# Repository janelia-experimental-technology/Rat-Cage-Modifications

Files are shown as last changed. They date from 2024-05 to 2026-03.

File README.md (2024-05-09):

# Rat-Cage-Modifications
Documents the process of modifying Tecniplast cage lids to better suit rats with electrophysiology implants.

Designed at HHMI's Janelia research campus by the jET team, the modifications allow more space inside the home cage for rats with head mounted electrophysiology implants. The cages as purchased position the water bottle spouts too low in areas of the cage where there is not enough space for the rats to comfortably drink.  

Advantages: More space for the rat to comfortably move around the cage. 

Construction: The cage modifications include cutting out the original bottle holder sections of the lid, and installing several machined, and sheetmetal parts that are riveted to the cage and sealed with epoxy. 

See the individual part drawings for more detail on fabricating each part. See the attached assembly files and instructions with parts list including purchased commercial items needed to complete the tcage modifications. There are two designs documented in this repo: the V1 rat cage lid modifications from 2018, and the V2 modifications implemented in 2021. The V1 changes are simpler and require fewer custom parts. However, the V1 water bottle holders do not last as long under autoclave sterilization as the V2 version. 

Operation: The cage can be used normally after modification, cleaned,  and sterilized via autoclave.

Opportunity: Free to make for Non-Profit Research by downloading the design here. See included hardware license.

Rights and designs available for Commercial License. Janelia makes no endorsements or guarantees of licensee products.

For inquiries, please contact innovation@janelia.hhmi.org and reference this repository.

To cite the designs, please use DOI: https://doi.org/10.25378/janelia.25750719

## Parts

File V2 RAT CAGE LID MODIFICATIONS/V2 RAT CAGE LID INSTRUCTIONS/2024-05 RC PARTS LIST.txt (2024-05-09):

Rat Cage Parts List
Main Folder: $/DATA/PROJECTS/_PROJECTS BY LAB/VIVARIUM/RAT CAGE MODIFICATIONS/
Quotes folder: */FINAL ORDER/QUOTES

1)	97524A030, Sealing Rivets, Aluminum, 0.063"-0.125", 100ct
	Qty: 18 for bottle-side, 10 for non-bottle-side, 28 total per cage 
	Desc: Binds metal brackets and bottle holder weldment to Ultem panels
	https://www.mcmaster.com/97524A030/

2)	97524A031, Sealing Rivets, Aluminum, 0.126"-0.187", 100ct
	Qty: 12 for each side, 24 total per cage
	Desc: Binds Ultem panels to cage lid. Back with 94589A617 washers to protect cage from cracking
	https://www.mcmaster.com/97524A031/

3)	94589A617, Washers, Aluminum, #4, 100ct
	Qty: 12 for each side, 24 total per cage
	Desc: Backed against 97524A031 rivets to protect plastic from cracking
	https://www.mcmaster.com/94589A617/

4)	7467A65, Adhesive, 3M DP125, 1.64oz, Gray
	Desc: Use to fill gap between panels and lid
	https://www.mcmaster.com/7467A65/

5)	7467A73, Taper Tip Mixer Nozzle for 1.64oz
	Desc: Use with DP125
	https://www.mcmaster.com/7467A73/

6)	7467A15, Air-powered Dispensing Gun
	https://www.mcmaster.com/7467A15/

7)	J009837, RC PANEL FRONT FOR BOTTLE
	Qty: 1 per cage
	Desc: Holds bottle holder weldment to cage lid
	Material: https://www.mcmaster.com/8685K44/
	Machining: made in house at HHMI, you will need to quote with machine shop

8)	J009838, RC PANEL SIDE
	Qty: 2 per cage
	Desc: Side pieces, 1 on each side of the cage lid
	Material: https://www.mcmaster.com/8685K44/
	Machining: made in house at HHMI, you will need to quote with machine shop

9)	J009859, RC PANEL FRONT
	Qty: 1 per cage
	Desc: Front panel, used on the end of the cage lid that doesn't hold a bottle
	Material: https://www.mcmaster.com/8685K44/
	Machining: made in house at HHMI, you will need to quote with machine shop

10)	J008644 revA, RCBH4 WELDMENT
	Qty: 1 per cage
	Desc: Bottle holder weldment. Mounts to J009837
	Reorder: GoProto 84701 for hardware, Able 7269-0-AAA for electropolishing
	Modifications: See Drawings

11)	J009835 RC BRACKET LONG
	Qty: 2 per cage
	Desc: Mounts RC PANEL SIDE to RC PANEL FRONT (FOR BOTTLE)
	Reorder: GoProto 85475

12)	J009836 RC BRACKET SIDE
	Qty: 2 per cage
	Desc: Mounts RC PANEL SIDE to rat cage lid
	Reorder: GoProto 85475

13)	J009600 RC BRACKET FRONT
	Qty: 2 per cage
	Desc: Mounts RC PANEL FRONT (FOR BOTTLE) to rat cage lid
	Reorder: GoProto 85475

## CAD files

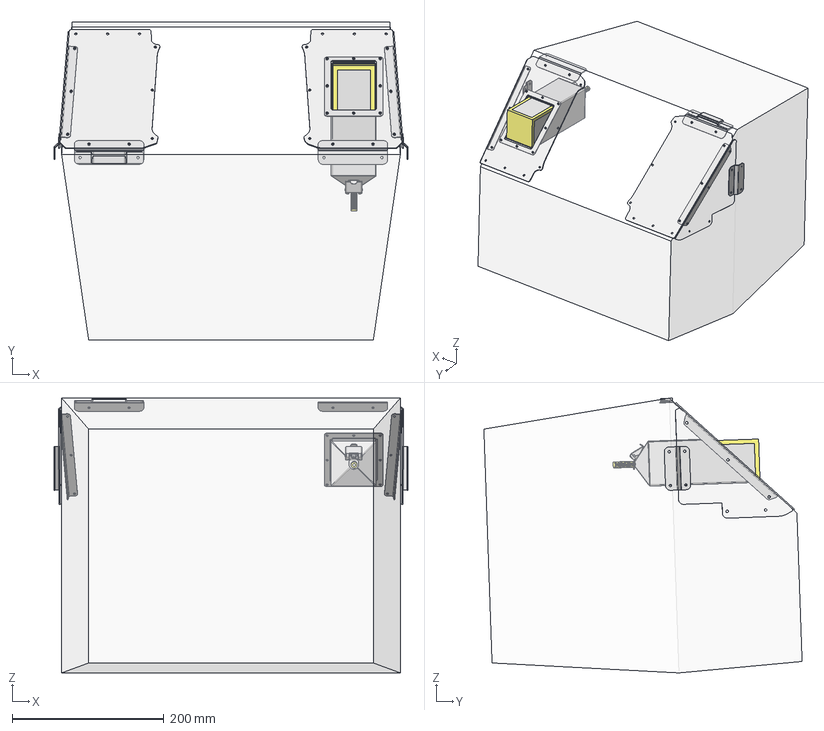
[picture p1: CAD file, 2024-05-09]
V2 RAT CAGE LID MODIFICATIONS/V2 RAT CAGE LID ASSEMBLY MODELS/RC ASSY.stp
465.9 x 418.9 x 361.7 mm
J009600 x 2
J009837
J009859
J009838 x 2
J008644_1
J008639 x 2
J008640
J008642
J008641
J008643
RAT CAGE
J009835 x 2
J009836 x 2
RAT CAGE BOTTLE
RAT CAGE FLAP COVER
RAT CAGE FLAP ROD
RAT CAGE FLAP SPRING
RAT CAGE FLAP
J010308

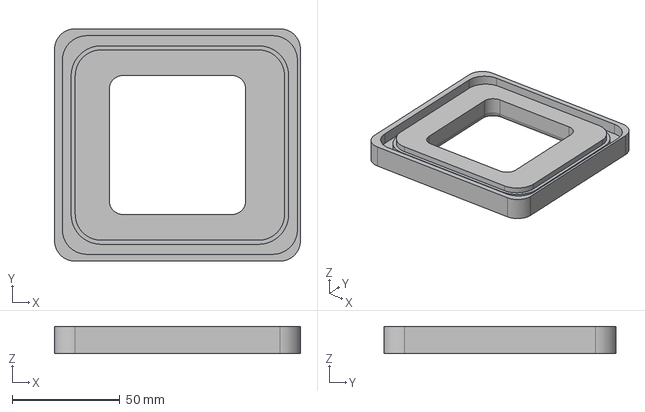
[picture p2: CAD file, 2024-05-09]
V1 RAT CAGE LID MODIFICATIONS/V1 RAT CAGE PART MODELS AND DRAWINGS/RAT WATER BOTTLE TRANSITION.stp
114.3 x 107.9 x 12.7 mm

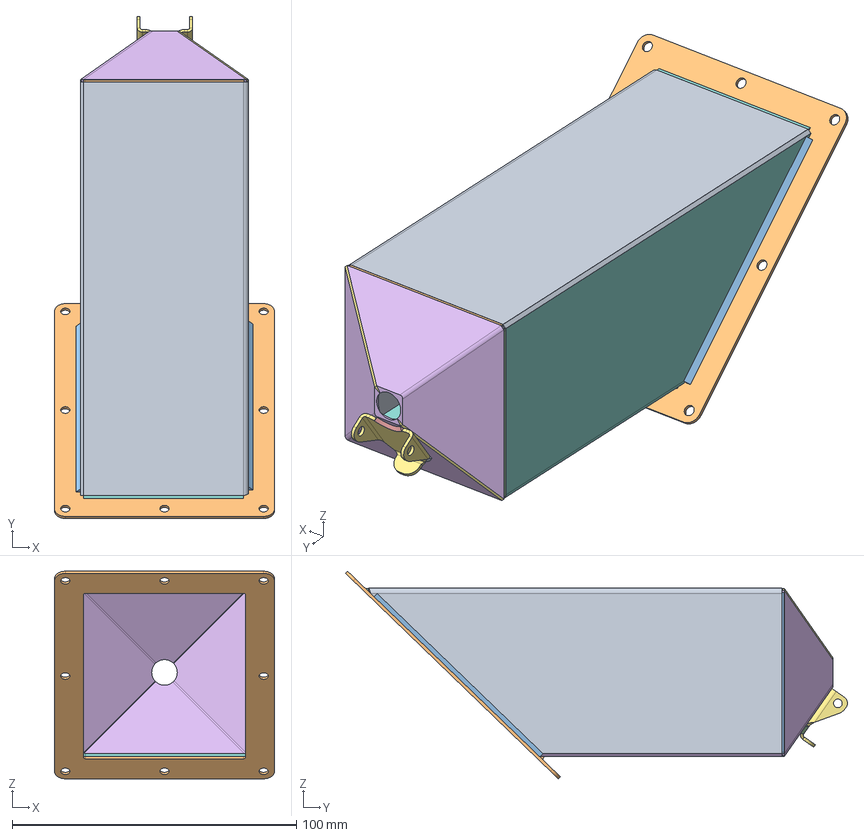
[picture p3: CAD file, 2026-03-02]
V2 RAT CAGE LID MODIFICATIONS/V2 RAT CAGE LID PART MODELS AND DRAWINGS/RCBH4 WELDMENT revC.stp
77.5 x 176.8 x 73.1 mm
J008644_1
J008639
J008640
J008642
J008641
J008639_1
J008643

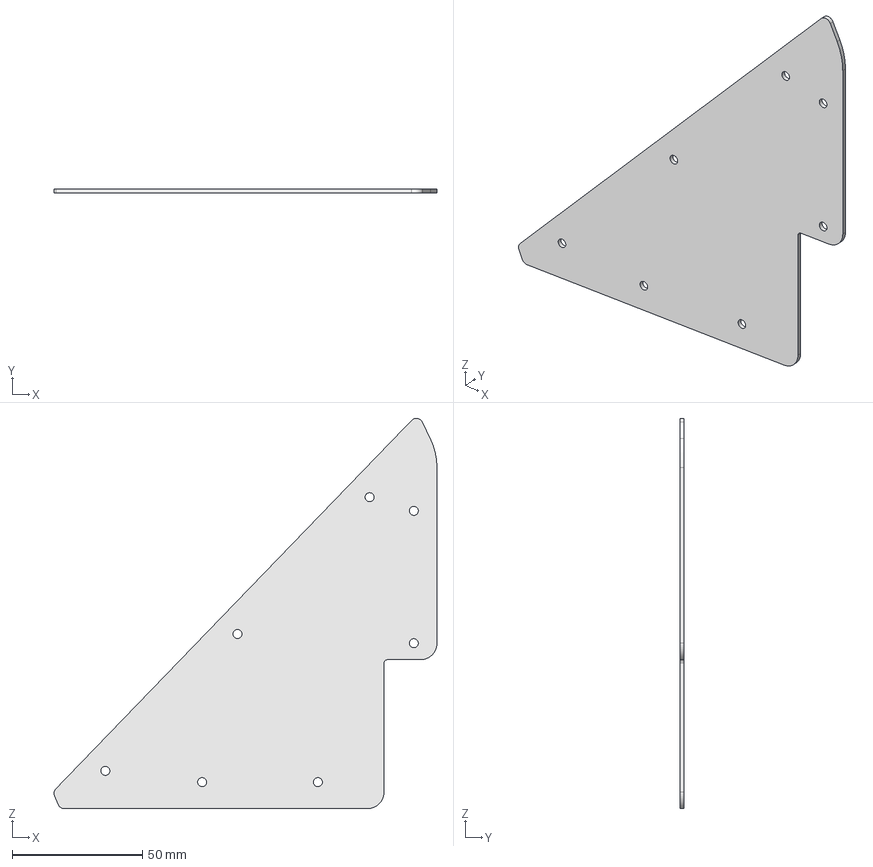
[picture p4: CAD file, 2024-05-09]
V1 RAT CAGE LID MODIFICATIONS/V1 RAT CAGE PART MODELS AND DRAWINGS/RC PANEL SIDE J009838.stp
147.0 x 1.59 x 149.8 mm

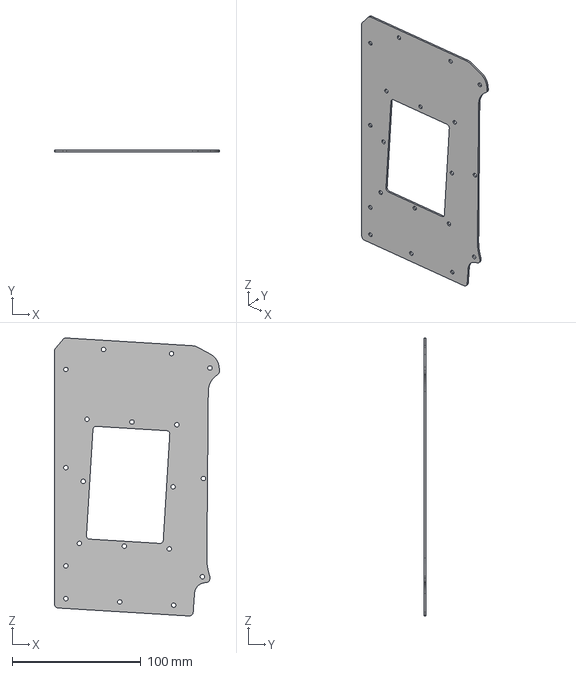
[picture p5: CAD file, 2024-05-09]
V2 RAT CAGE LID MODIFICATIONS/V2 RAT CAGE LID PART MODELS AND DRAWINGS/RC PANEL FRONT FOR BOTTLE J009837.stp
128.1 x 1.59 x 215.7 mm

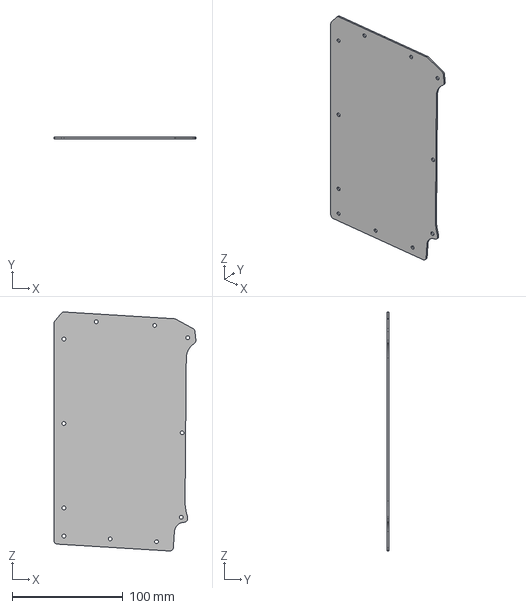
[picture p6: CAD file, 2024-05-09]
V1 RAT CAGE LID MODIFICATIONS/V1 RAT CAGE PART MODELS AND DRAWINGS/RC PANEL FRONT J009859.stp
128.1 x 1.59 x 215.7 mm

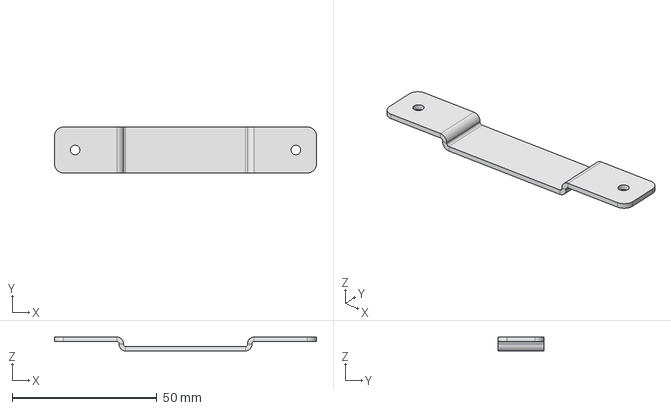
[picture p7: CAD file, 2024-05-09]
V1 RAT CAGE LID MODIFICATIONS/V1 RAT CAGE PART MODELS AND DRAWINGS/CARD HOLDER BRACKET J010308.stp
90.4 x 15.9 x 4.83 mm

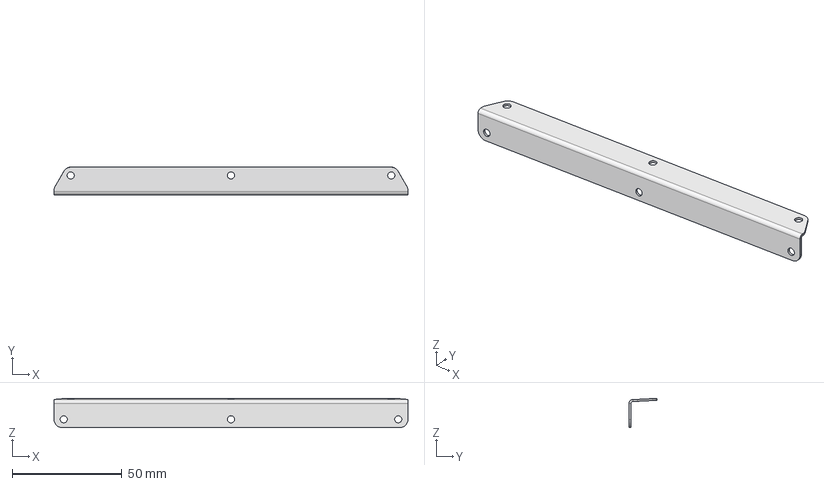
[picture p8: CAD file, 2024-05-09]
V1 RAT CAGE LID MODIFICATIONS/V1 RAT CAGE PART MODELS AND DRAWINGS/RC BRACKET LONG.stp
161.3 x 12.7 x 13.4 mm

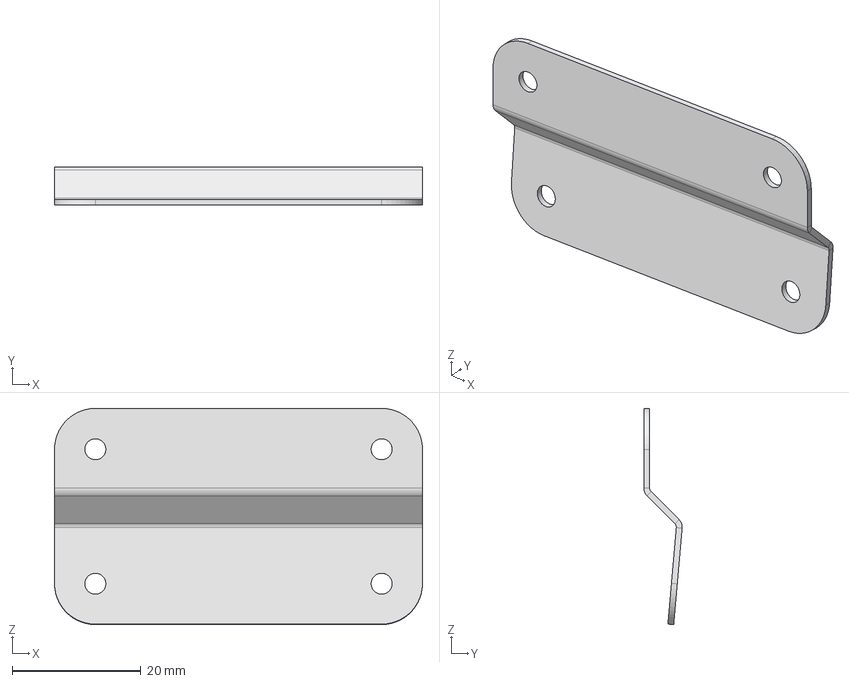
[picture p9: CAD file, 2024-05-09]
V1 RAT CAGE LID MODIFICATIONS/V1 RAT CAGE PART MODELS AND DRAWINGS/RC BRACKET SIDE.stp
57.1 x 5.97 x 33.6 mm

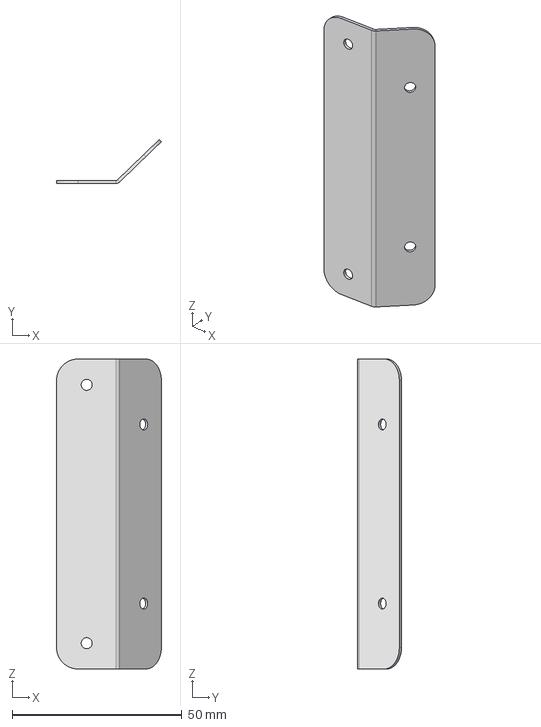
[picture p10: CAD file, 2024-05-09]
V1 RAT CAGE LID MODIFICATIONS/V1 RAT CAGE PART MODELS AND DRAWINGS/RC BRACKET FRONT.stp
30.9 x 13.0 x 91.4 mm

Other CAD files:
V2 RAT CAGE LID MODIFICATIONS/V2 RAT CAGE LID PART MODELS AND DRAWINGS/RCBH4 WELDMENT.dwg
V2 RAT CAGE LID MODIFICATIONS/V2 RAT CAGE LID PART MODELS AND DRAWINGS/RC PANEL FRONT FOR BOTTLE.dwg
V1 RAT CAGE LID MODIFICATIONS/V1 RAT CAGE PART MODELS AND DRAWINGS/RC PANEL FRONT.dwg
V1 RAT CAGE LID MODIFICATIONS/V1 RAT CAGE PART MODELS AND DRAWINGS/RC PANEL SIDE.dwg
V1 RAT CAGE LID MODIFICATIONS/V1 RAT CAGE PART MODELS AND DRAWINGS/CARD HOLDER BRACKET.dwg
V1 RAT CAGE LID MODIFICATIONS/V1 RAT CAGE PART MODELS AND DRAWINGS/CARD HOLDER BRACKET.ipt
V1 RAT CAGE LID MODIFICATIONS/V1 RAT CAGE PART MODELS AND DRAWINGS/RAT WATER BOTTLE TRANSITION.dwg
V1 RAT CAGE LID MODIFICATIONS/V1 RAT CAGE PART MODELS AND DRAWINGS/RAT WATER BOTTLE TRANSITION.ipt
V1 RAT CAGE LID MODIFICATIONS/V1 RAT CAGE PART MODELS AND DRAWINGS/RC BRACKET FRONT.dwg
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

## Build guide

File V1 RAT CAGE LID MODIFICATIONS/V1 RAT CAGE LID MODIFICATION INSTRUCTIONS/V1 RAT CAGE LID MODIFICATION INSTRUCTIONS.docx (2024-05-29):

Rat Cage Lid Modification Procedure

Parts List:

Name | Part Number | Vendor / Part Type | Qty / Unit
Rat Cage Lid | | Purchased-Techniplast | 1
RC Panel Front | J009859 | Custom machined | 1
RC Panel Side | J009838 | Custom machined | 1
RC Bracket Front | J009600 | Custom sheetmetal-GoProto | 1
RC Bracket Long | J009835 | Custom sheetmetal-GoProto | 1
RC Bracket Side | J009836 | Custom sheetmetal-GoProto | 1
Card Holder Bracket | J010308 | Custom sheetmetal-GoProto | 1
bottom taper section of right water bottle holder | | Purchased-Part of Techniplast Lid | 1
Rat Water Bottle Transition | | Custom machined | 1
Rivets - .063” - .125” | 97447A015 | McMaster | 10
Rivets - .126” - .187” | 97447A020 | McMaster | 10
Rivets - .188” - .25” | 97447A025 | McMaster | 2
18-8 SS No. 4 Washer | 98019A309 | McMaster | 8
18-8 SS No. 5 Washer | 90945A712 | McMaster | 10
Epoxy, 3M DP125 | 7467A65 | McMaster | 1

Tools List:

Name | Part Number | Vendor | Quantity/Unit
Angle Grinder/Dremel
1/8” Drill Bit
#28 Drill Bit

Power Drill
Pliers
Epoxy Applicator Gun | 74695A71 | McMaster | 1
Masking Tape | | | 1
Binder Clips (optional) | | | 2

Procedure

1. Cut Cage Lid
  a. Cut water bottle holder sections off the lid – cut lines shown in red on right picture
  b. The left and right sides will be cut at different locations

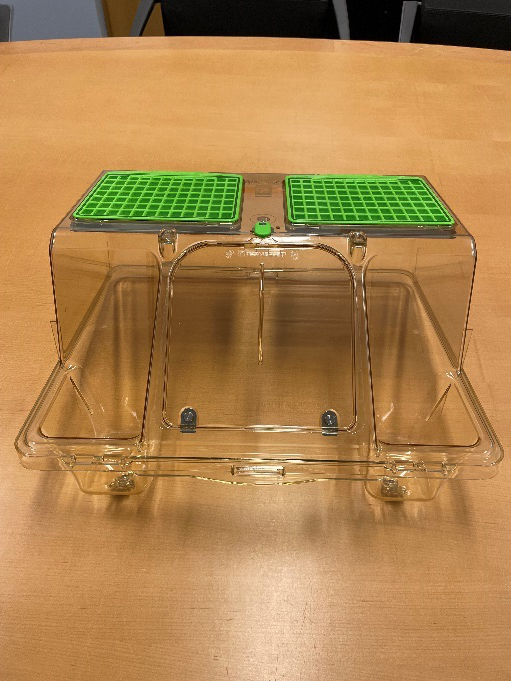
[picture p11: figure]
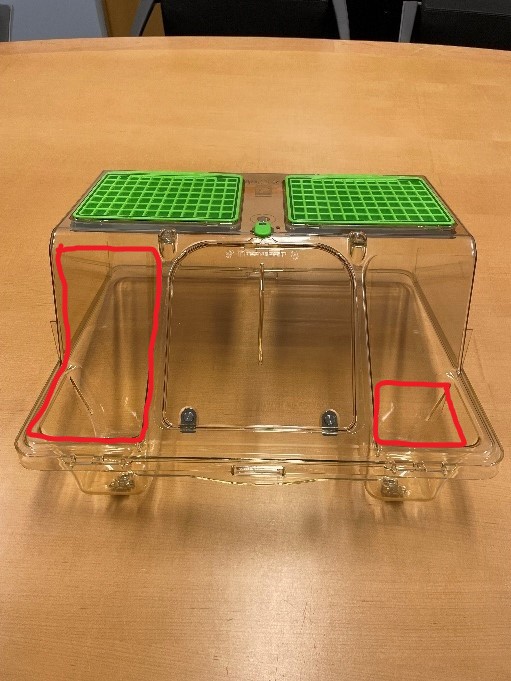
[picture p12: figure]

  c. Cut right bottle holder section at thick red line in photo below – there will be a natural seam to follow
  d. Save the bottom taper section of the holder and metal flap assembly and for reattachment to modified cage

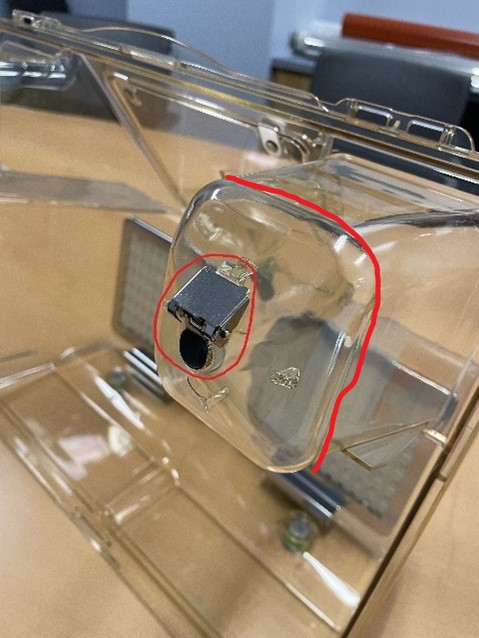
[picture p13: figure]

  e. Grind off the front card holder on the left side of the cage

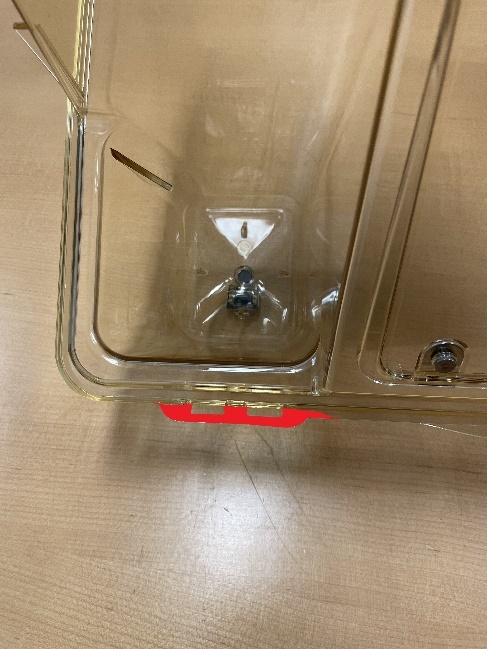
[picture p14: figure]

2. Assemble Flat Cover

Parts:

Part Number | Quantity
J009859 | 1
J009838 | 1
J009600 | 1
J009835 | 1
J009836 | 1
97447A015 | 10
90945A712 | 2

  a. Rivet front panel (J009859) and side panel (J009838) together using the long bracket (J009835) and six 97447A015 rivets
    i. Proper orientation of the panels, with respect to each other:

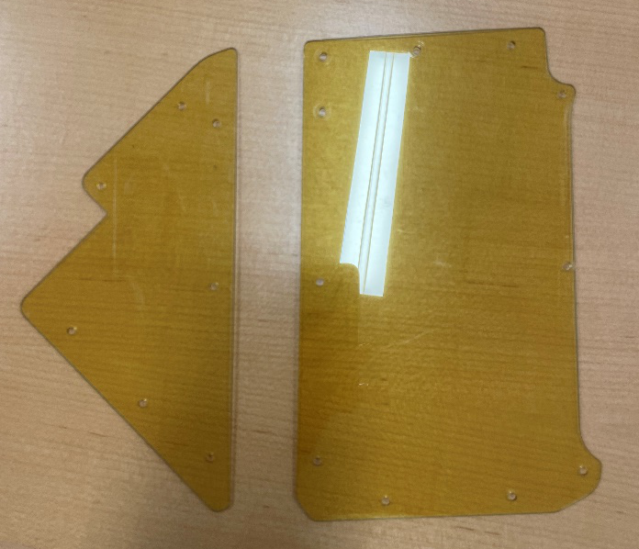
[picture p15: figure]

    ii. The bracket is not symmetrical – the side with square corners should be attached to the front panel
    iii. Bracket should be attached on the inside of the panels, with rivets attached from the outside, so the flat head is on the outside of the plastic

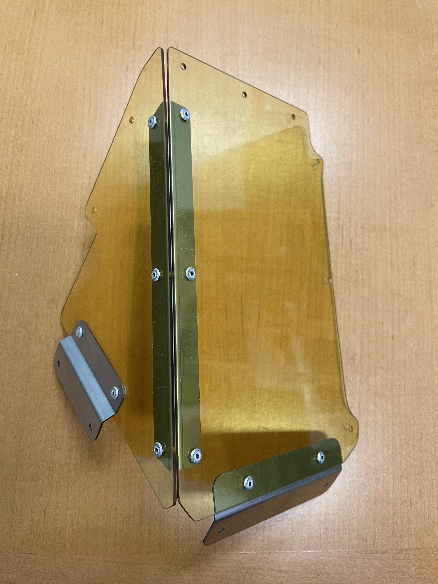
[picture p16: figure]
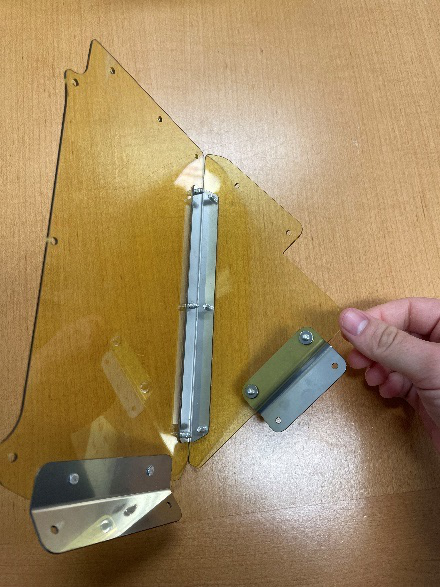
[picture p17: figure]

  b. Rivet front bracket (J009600) to the front panel with two 97447A015 rivets
    i. Bracket should be on the inside of the panel, with the bracket extending down below the panel
    ii. Rivets attached from the outside, so the flat head is on the outside of the plastic

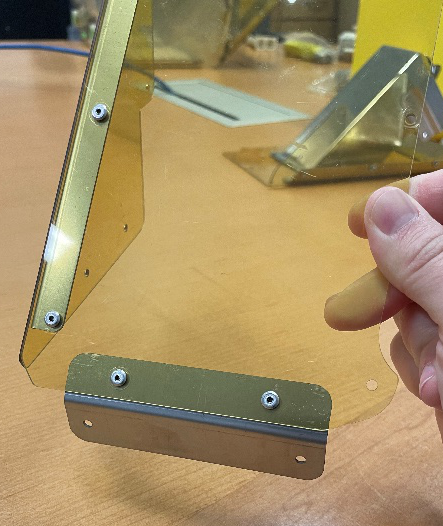
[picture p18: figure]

  c. Rivet side bracket (J009836) to the side panel with two 97447A015 rivets
    i. Bracket should be on the outside of the panel, with the short side of the “z” attached to the panel and the bracket jutting out away from the panel
    ii. Rivets will be attached through the bracket into the panel – use two washers (90945A712) behind the panel

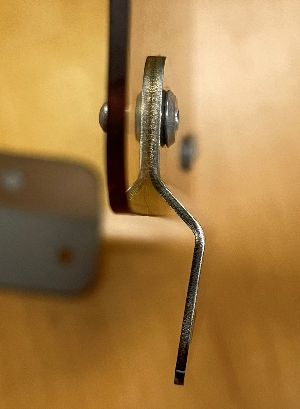
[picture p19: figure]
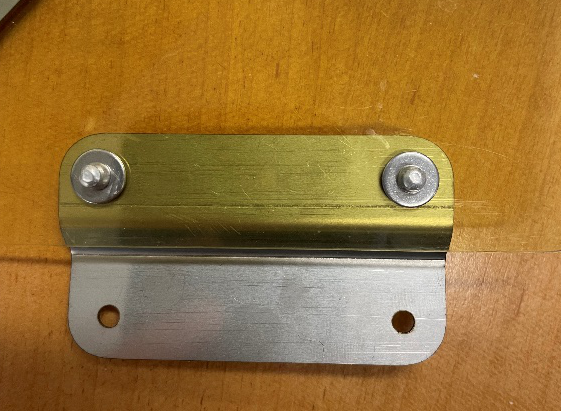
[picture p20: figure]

3. Attach Flat Cover Assembly to Cage

Parts:

Part Number | Quantity
97447A020 | 10
90945A712 | 8
J010308 | 1
97447A025 | 2

  a. Use cover assembly as guides to drill mounting holes through cage lid – hole locations marked in red
    i. Flat panel assembly mounts on left side of lid when looking at the front
    ii. Drill initial holes with 1/8” drill bit

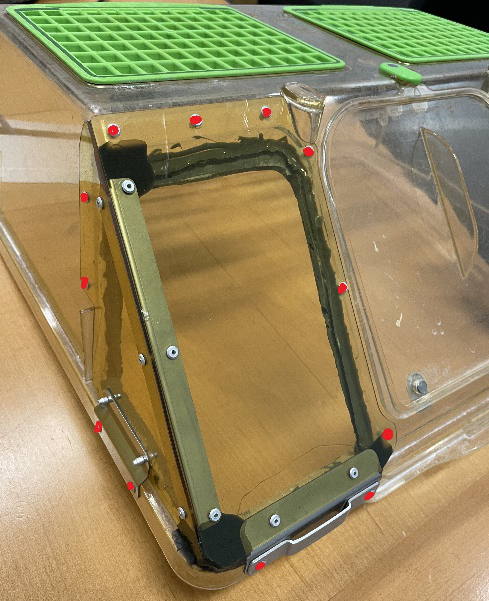
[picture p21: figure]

    iii. Can be helpful to hold the cover assembly in place with binder clips while drilling
  b. Remove cover assembly and enlarge holes with #28 drill bit
  c. Attach cover assembly to lid
    i. The eight rivets going through the front and side walls, as opposed to the bottom rim, should have backing washers behind the lid plastic – locations shown in red

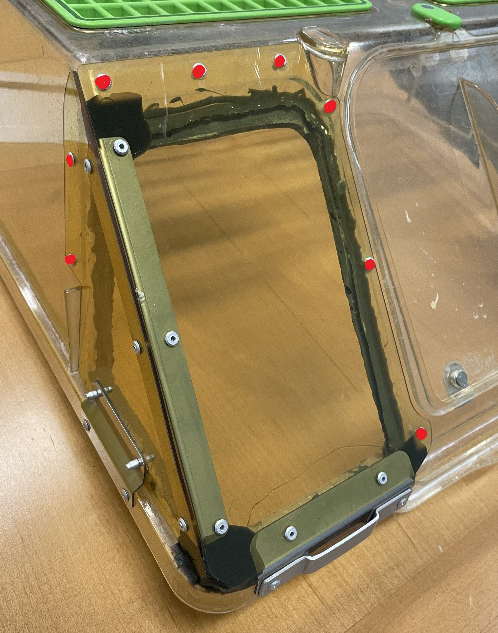
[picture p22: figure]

    ii. The washer for the hole circled in blue will need to be cut into a D-ring to fit in the compressed space along the thin wall

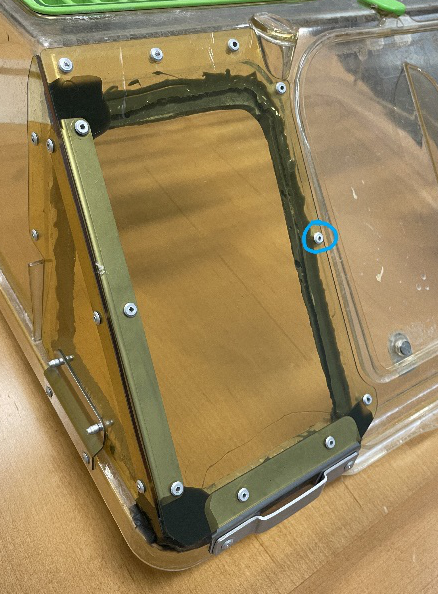
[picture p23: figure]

    iii. The card holder bracket (J010308) should be riveted to the front lip of the lid along with the cover using two 97447A025 rivets

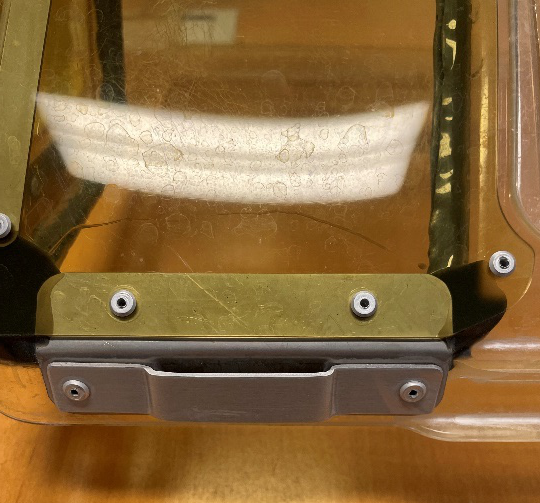
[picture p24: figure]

    iv. At all ten other points of attachment, the 97447A020 rivets are sufficient
    v. The two rivets through the bottom lip on the left side of the lid need to be ground flush to the plastic on the inside of the lid

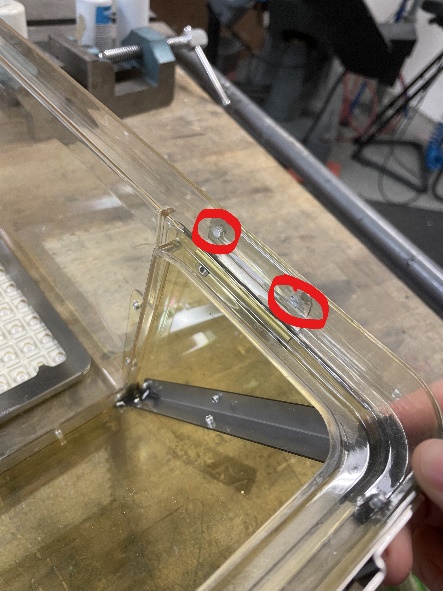
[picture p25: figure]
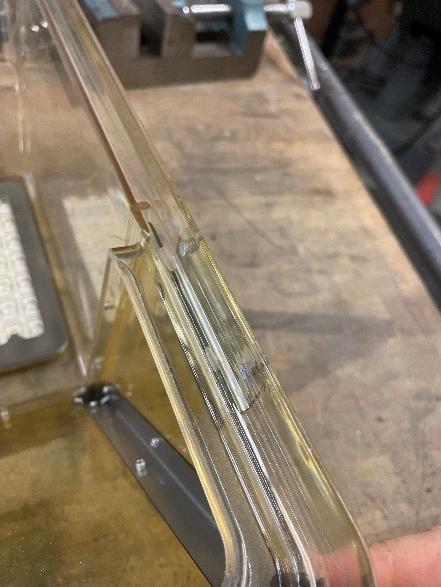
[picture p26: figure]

4. Assemble Water Bottle Holder Cover and Attach to Cage

Parts:

Part | Quantity
rat water bottle transition | 1
bottom taper section of right water bottle holder | 1

  a. Epoxy bottom taper section of right water bottle holder to the bottom of the machined rat water bottle transition part

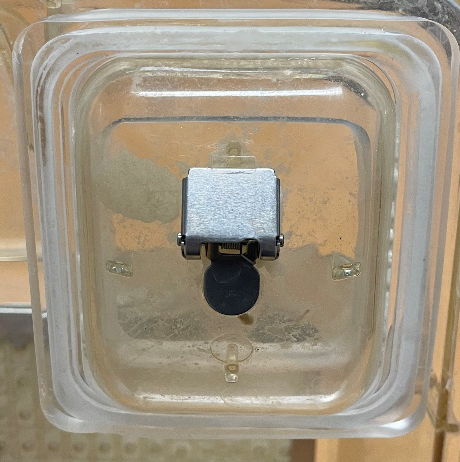
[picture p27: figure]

  b. Epoxy this combined part onto the rest of the cage where the right water bottle holder was originally located

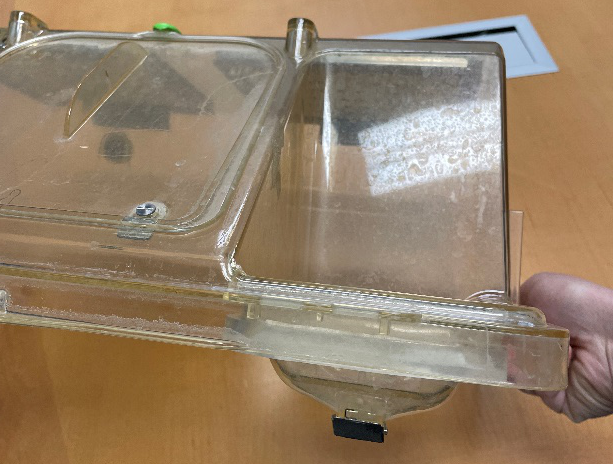
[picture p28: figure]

5. Epoxy
  a. Seal the corners of the covers with epoxy (7467A65)
    i. Circled corners need epoxy

Note: There is epoxy all the way around the cut opening in the left side of the lid in these photos – that is leftover from a different modification. Do not replicate this

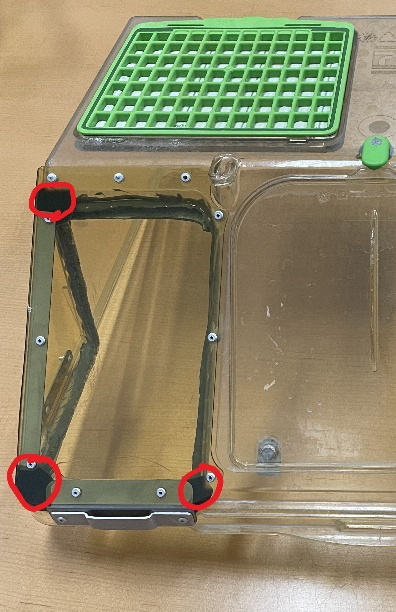
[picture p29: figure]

    ii. Tape over the openings

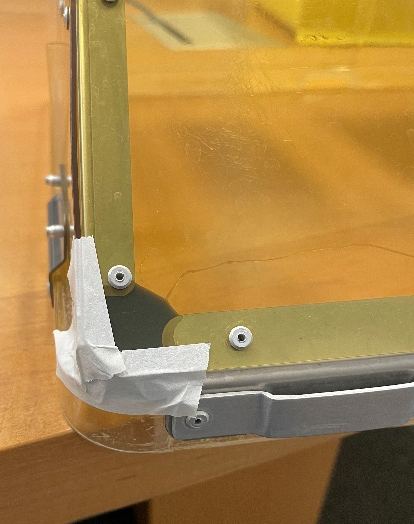
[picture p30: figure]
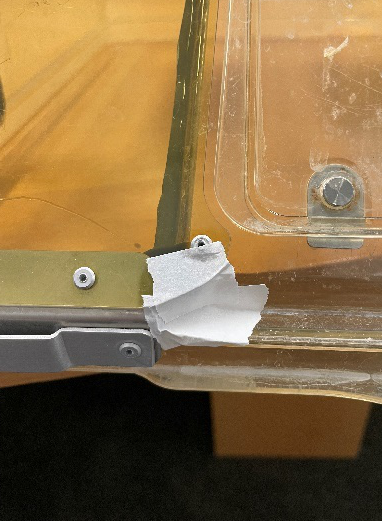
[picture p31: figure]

    iii. Inject epoxy with applicator gun from the inside of the lid

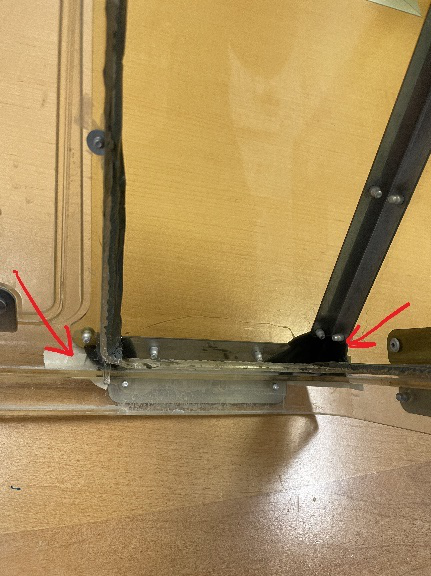
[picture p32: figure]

    iv. Stand on end to prevent epoxy from running and let dry 24 hours before removing tape

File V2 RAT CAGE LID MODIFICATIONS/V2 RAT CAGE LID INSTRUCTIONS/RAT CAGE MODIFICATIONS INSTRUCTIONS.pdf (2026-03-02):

Rat Cage Lid Modification Procedure

Parts List:

Name | Part Number | Vendor / Part Type | Qty / Unit
Rat Cage Lid | | Purchased-Techniplast | 1
RC Panel Front | J009859 | Custom machined | 1
RC Panel Front for Bottle | J009837 | Custom machined | 1
RC Panel Side | J009838 | Custom machined | 2
RCBH4 Weldment | J008644 | Custom weldment-GoProto | 1
RC Bracket Front | J009600 | Custom sheetmetal-GoProto | 2
RC Bracket Long | J009835 | Custom sheetmetal-GoProto | 2
RC Bracket Side | J009836 | Custom sheetmetal-GoProto | 2
Card Holder Bracket | J010308 | Custom sheetmetal-GoProto | 1
Rat Cage Flap Assembly | | Purchased-Part of Techniplast Lid | 1
Rivets - .063” - .125” | 97447A015 | McMaster | 28
Rivets - .126” - .187” | 97447A020 | McMaster | 22
Rivets - .188” - .25” | 97447A025 | McMaster | 2
18-8 SS No. 4 Washer | 98019A309 | McMaster | 8
18-8 SS No. 5 Washer | 90945A712 | McMaster | 20
Epoxy, 3M DP125 | 7467A65 | McMaster | 1
Spacer, 2mm Thk | 92871A102 | McMaster | 2 ( As needed)

Tools List:

Name | Part Number | Vendor | Quantity/Unit
Angle Grinder/Dremel
1/8” Drill Bit
#28 Drill Bit

Power Drill
Pliers
Epoxy Applicator Gun | 74695A71 | McMaster | 1
Masking Tape | | | 1
Binder Clips (optional) | | | 2

Procedure

1. Cut Cage Lid
a. Cut water bottle holder sections off the lid – cut lines shown in red on right picture

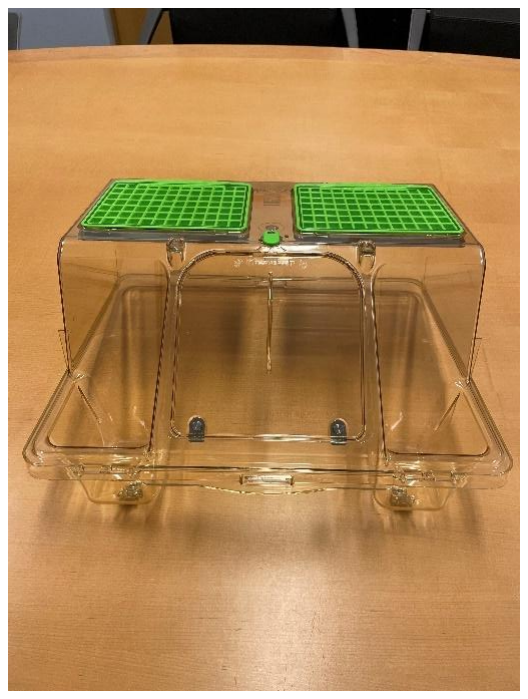
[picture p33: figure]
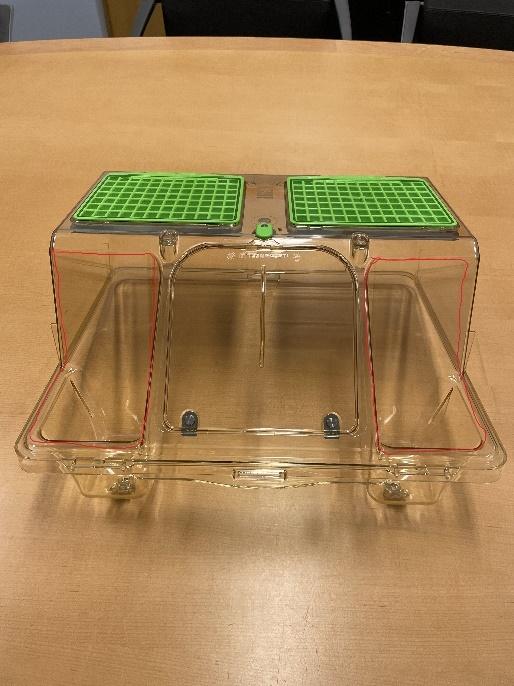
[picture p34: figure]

b. Save metal flap assembly for reattachment to modified cage – there should be four components
i. Axle, spring, axle-mounted flap, large rectangular cover

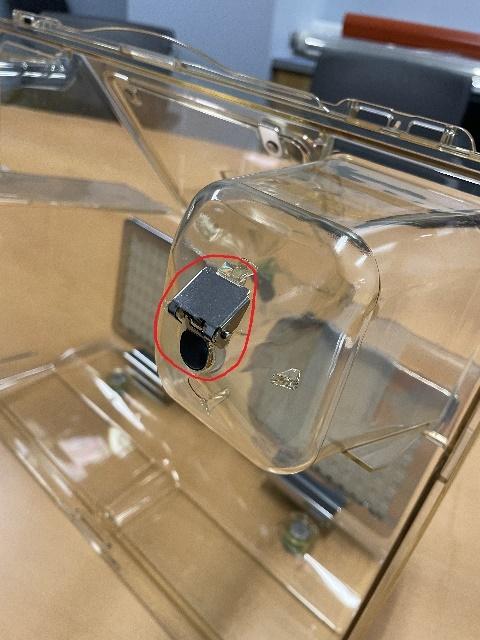
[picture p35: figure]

c. Grind off both card holders on the front

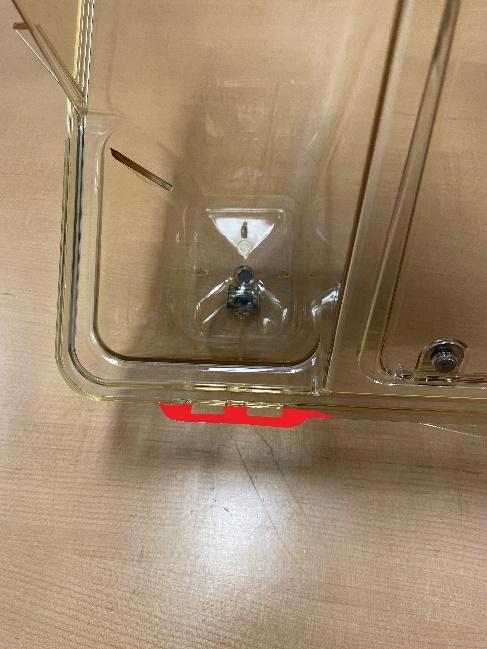
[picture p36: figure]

2. Assemble Flat Cover
Parts:
Part Number | Quantity
J009859 | 1
J009838 | 1
J009600 | 1
J009835 | 1
J009836 | 1
97447A015 | 10
90945A712 | 2
a. Rivet front panel (J009859) and side panel (J009838) together using the long bracket (J009835) and six 97447A015 rivets
i. Proper orientation of the panels, with respect to each other:

ii. The bracket is not symmetrical – the side with square corners should be attached to the front panel
iii. Bracket should be attached on the inside of the panels, with rivets attached from the outside, so the flat head is on the outside of the plastic

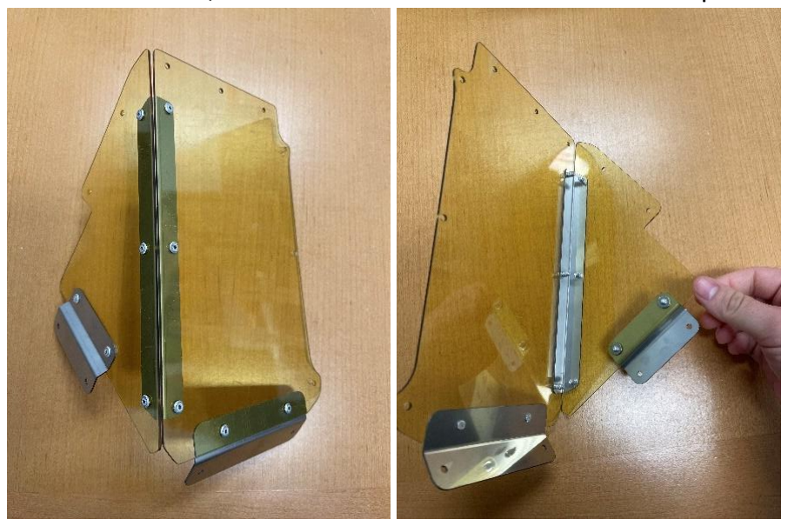
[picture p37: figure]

b. Rivet front bracket (J009600) to the front panel with two 97447A015 rivets
i. Bracket should be on the inside of the panel, with the bracket extending down below the panel
ii. Rivets attached from the outside, so the flat head is on the outside of the plastic

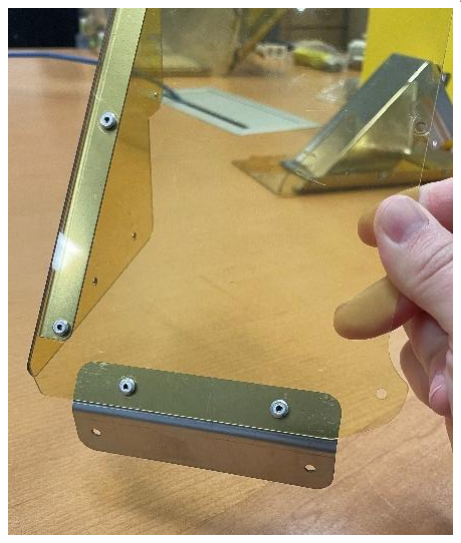
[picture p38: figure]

c. Rivet side bracket (J009836) to the side panel with two 97447A015 rivets
i. Bracket should be on the outside of the panel, with the short side of the “z” attached to the panel and the bracket jutting out away from the panel
ii. Rivets will be attached through the bracket into the panel – use two washers (90945A712) behind the panel

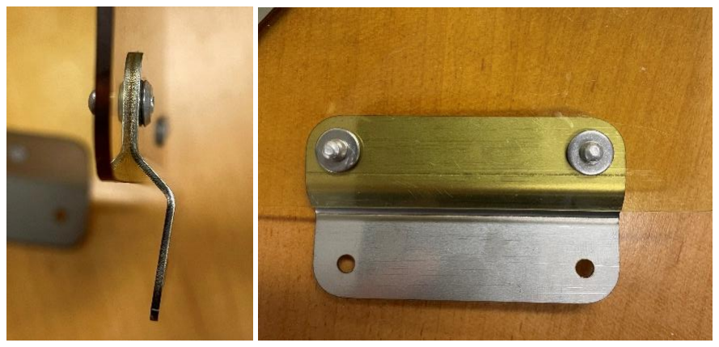
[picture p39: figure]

3. Assemble Water Bottle Holder Cover Parts:
Part Number | Quantity
J009837 | 1
J009838 | 1
J008644 | 1
J009600 | 1
J009835 | 1
J009836 | 1
97447A015 | 18
90945A712 | 2
98019A309 | 8
92871A102 | 2 ( As needed)
Cage Flap Assembly Parts | 1 ea. axle, spring, flap, cover
a. Attach RCBH4 Weldment (J008644) to the front panel (J009837) in the orientation shown here using eight 97447A015 rivets

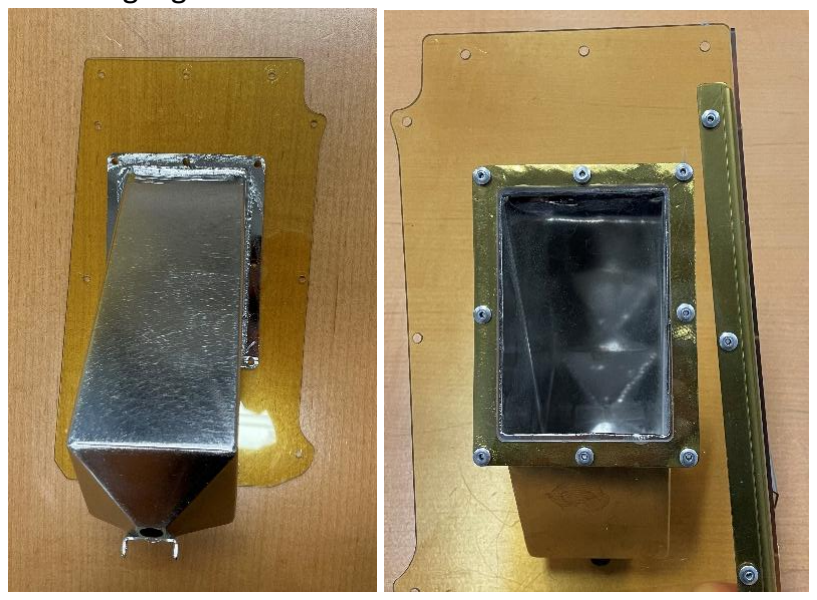
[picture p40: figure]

b. Rivet front panel and side panel (J009838) together using the long bracket (J009835) and six 97447A015 rivets
i. Proper orientation of the panels, with respect to each other:

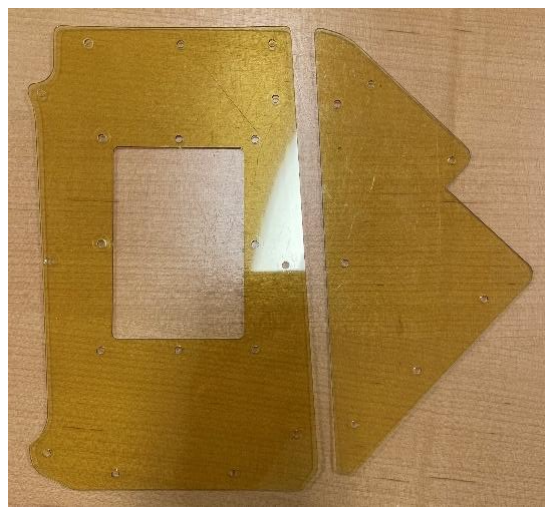
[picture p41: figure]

ii. The bracket is not symmetrical – the side with square corners should be attached to the front panel
iii. Bracket should be attached on the inside of the panels, with rivets attached from the outside, so the flat head is on the outside of the plastic
c. Rivet front bracket (J009600) to the front panel with two 97447A015 rivets
i. Bracket should be on the inside of the panel, with the bracket extending down below the panel
ii. Rivets attached from the outside, so the flat head is on the outside of the plastic

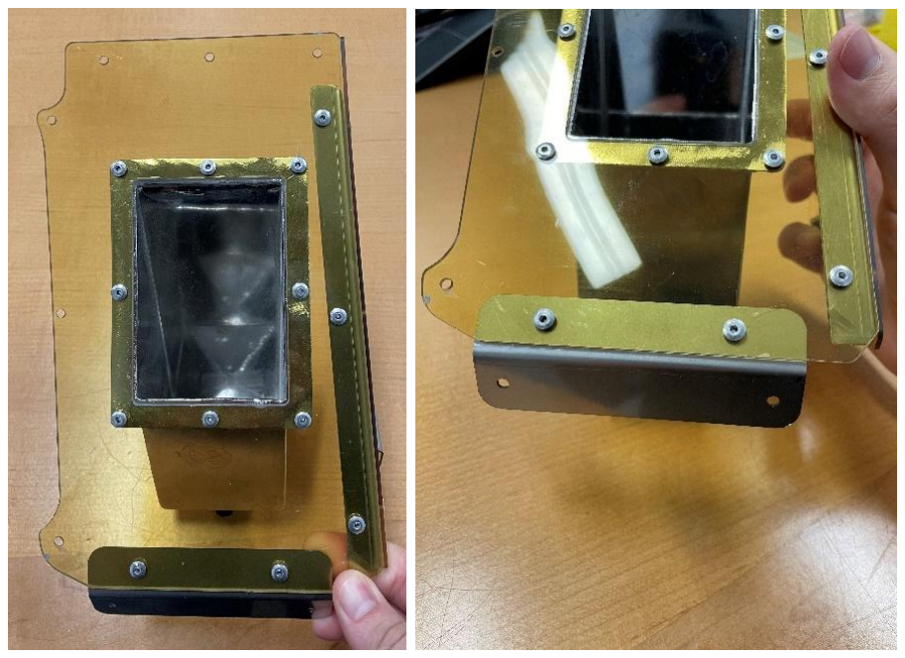
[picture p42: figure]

d. Rivet side bracket (J009836) to the side panel with two 97447A015 rivets
i. Bracket should be on the outside of the panel, with the short side of the “z” attached to the panel and the bracket jutting out away from the panel
ii. Rivets will be attached through the bracket into the panel – use two washers (90945A712) behind the panel

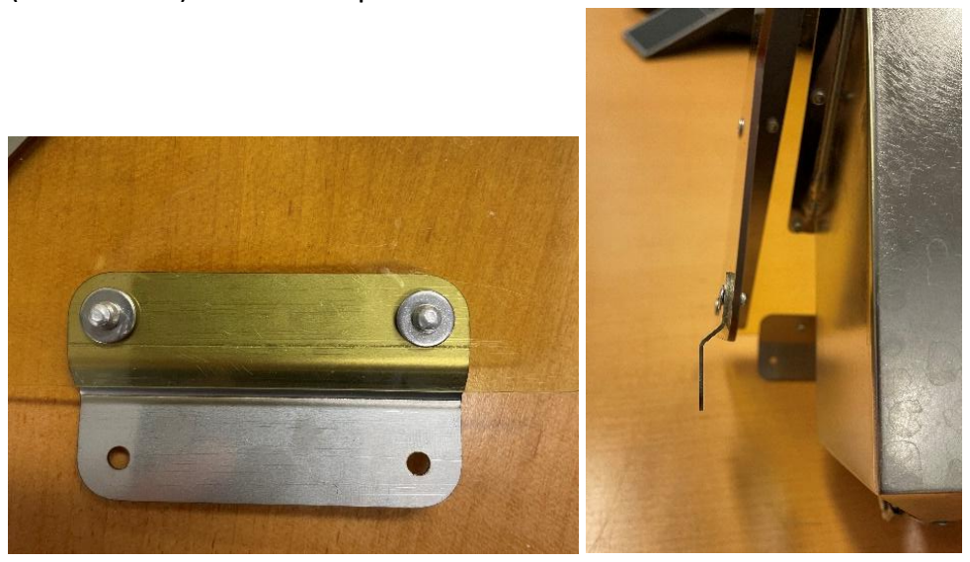
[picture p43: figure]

e. Attach cover flap assembly to weldment
i. Axle spans the two tabs on the weldment, below the through hole for the water bottle tip
ii. Eight 98019A309 washers should sandwich the flap and spring, four on either side, to keep the flap and spring centered over the through hole. To save time and ease assembly, one single 92871A102 spacer can be inserted on either side of the flap in place of the washers.

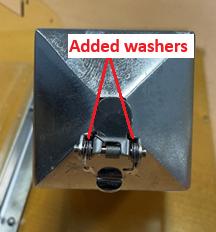
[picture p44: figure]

iii. Cover should snap into grooves in the axle and click into place

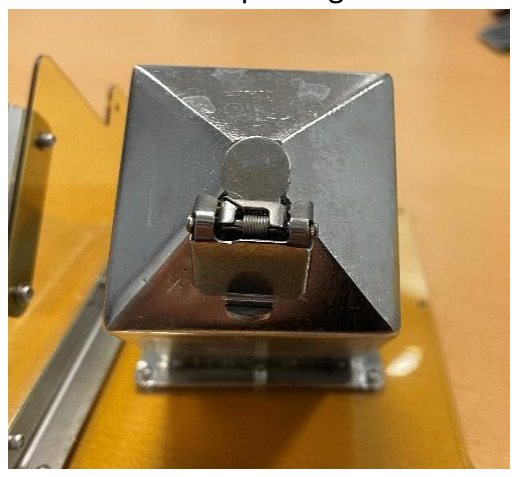
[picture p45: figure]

iv. Bend tab over far enough to ensure cover will stay in place.

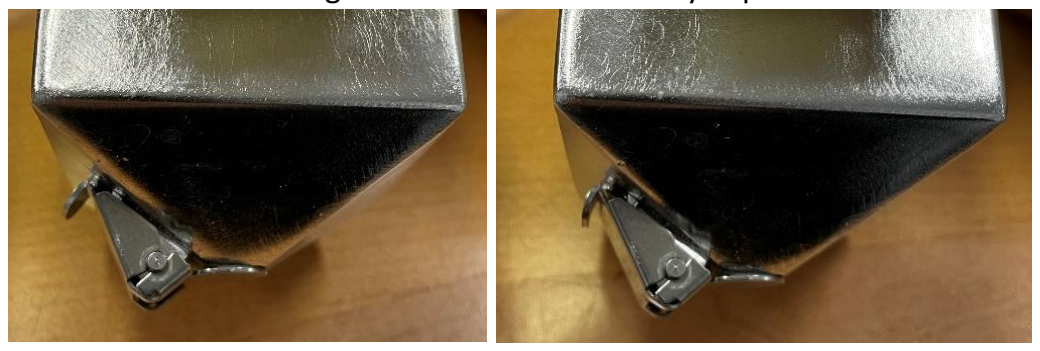
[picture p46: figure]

4. Attach Water Bottle Cover Assembly to Cage Parts:
Part Number | Quantity
97447A020 | 12
90945A712 | 8
a. Use cover assembly as guides to drill mounting holes through cage lid – hole locations marked in red
i. Water bottle holder assembly mounts on right side of lid when looking at the front
ii. Drill initial holes with 1/8” bit

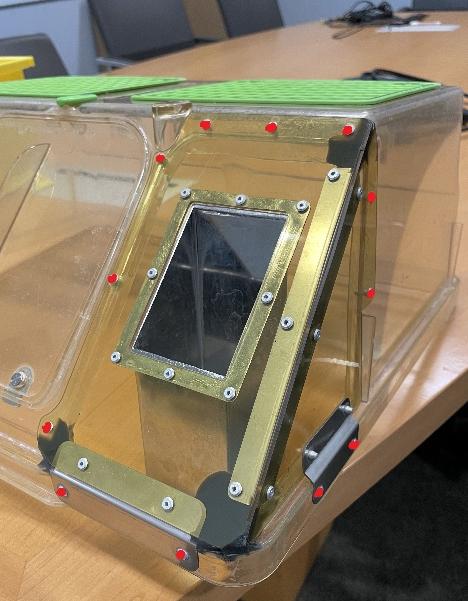
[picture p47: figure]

iii. Can be helpful to hold the cover assembly in place with binder clips while drilling

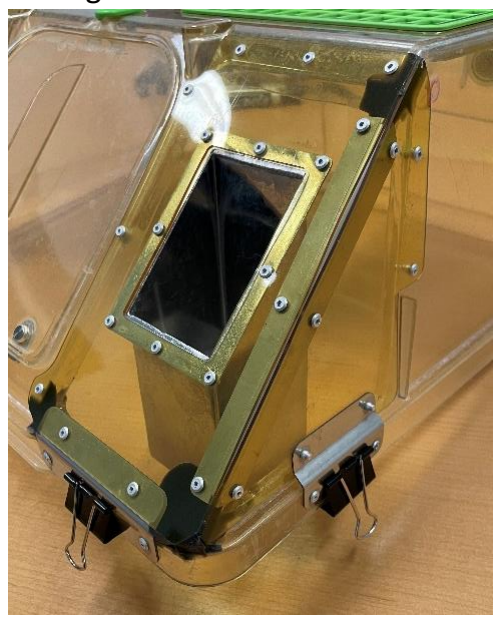
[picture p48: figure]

b. Remove cover assembly and enlarge holes with #28 drill bit
c. Attach cover assembly to lid using twelve 97447A020 rivets
i. The eight rivets going through the front and side walls of the cage lid, as opposed to the bottom rim, should have backing washers (90945A712) behind the lid – locations shown in red. The rivets going through the bottom rim should be installed from the inside.

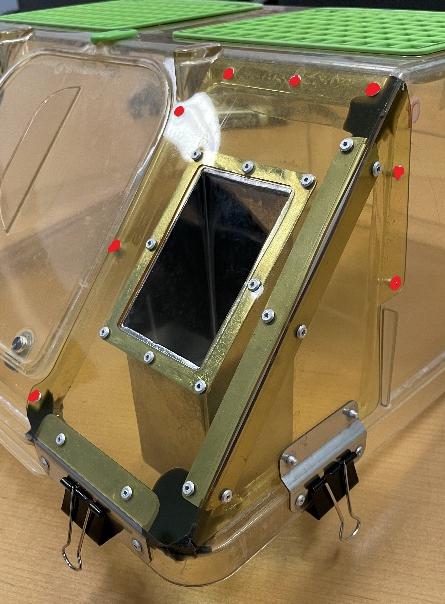
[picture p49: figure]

ii. The washer for the hole circled in blue will need to be cut into a D-ring to fit in the compressed space along the thin wall

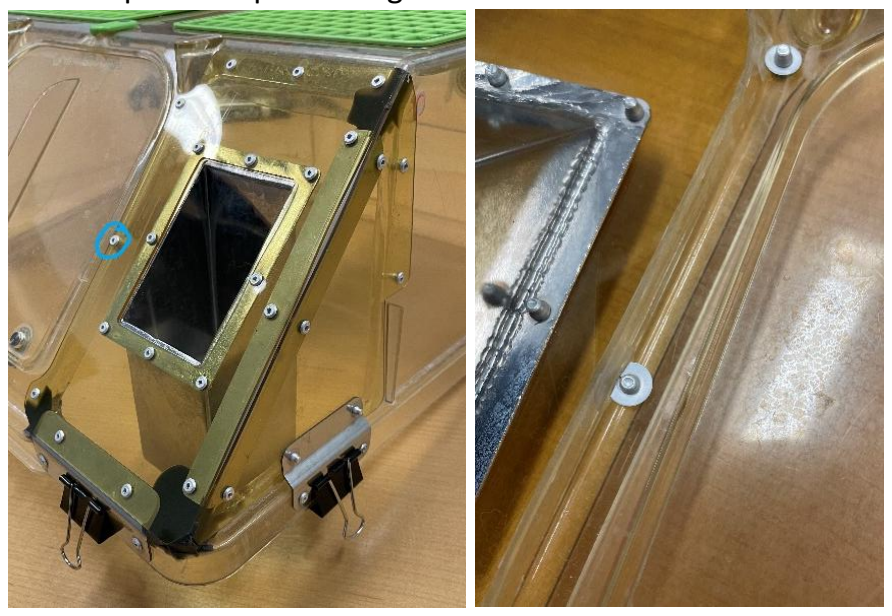
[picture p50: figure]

iii. The two rivets through the bottom lip on the right side of the lid need to be installed from the inside. Grind the rivets down on the outside after riveting.

5. Attach Flat Cover Assembly to Cage Parts:
Part Number | Quantity
97447A020 | 10
90945A712 | 8
J010308 | 1
97447A025 | 2
a. Use cover assembly as guides to drill mounting holes through cage lid – hole locations marked in red
i. Flat panel assembly mounts on left side of lid when looking at the front
ii. Drill initial holes with 1/8” drill bit


iii. Can be helpful to hold the cover assembly in place with binder clips while drilling
b. Remove cover assembly and enlarge holes with #28 drill bit if needed to install rivets.
c. Attach cover assembly to lid
i. The eight rivets going through the front and side walls, as opposed to the bottom rim, should have backing washers behind the lid plastic – locations shown in red. The rivets going through the bottom rim should be installed from the inside.


ii. The washer for the hole circled in blue will need to be cut into a D-ring to fit in the compressed space along the thin wall


iii. The card holder bracket (J010308) should be riveted to the front lip of the lid along with the cover using two 97447A025 rivets


iv. At all ten other points of attachment, the 97447A020 rivets are sufficient v. The two rivets through the bottom lip on the left side of the lid need to be installed from the inside. Grind the rivets down on the outside of the cage after installation.

6. Epoxy


a. Seal the corners of the covers with epoxy (7467A65)
i. Circled corners need epoxy
Note: There is epoxy all the way around the cut opening in the left side of the lid in these photos – that is leftover from a different modification. Do not replicate this


ii. Tape over the openings

iii. Inject epoxy with applicator gun from the inside of the lid

iv. Stand on end to prevent epoxy from running and let dry 24 hours before removing tape
v. After epoxy has dried remove tape and examine the outer surfaces of the cage for sharp edges created by sagging epoxy. Sand any sharp edges that could cut skin or tear gloves.

Revision History
DATE | INITIALS | DESCRIPTION
8/4/2025 | JBA | Added note about sanding sharp edges and pointed out flap spacer washers
9/23/2025 | JBA | Add better images and descriptions re: washers and rivet install direction on lower lid flange, to be installed from inside.
02/05/2026 | JBA | Add notes regarding rivets installed from the inside of cage top lower lip. The rivets should be ground down on the outside to ensure cage rack clearance.
03/02/2026 | JBA | Add alternate spacer option to replace 4 washers on flap

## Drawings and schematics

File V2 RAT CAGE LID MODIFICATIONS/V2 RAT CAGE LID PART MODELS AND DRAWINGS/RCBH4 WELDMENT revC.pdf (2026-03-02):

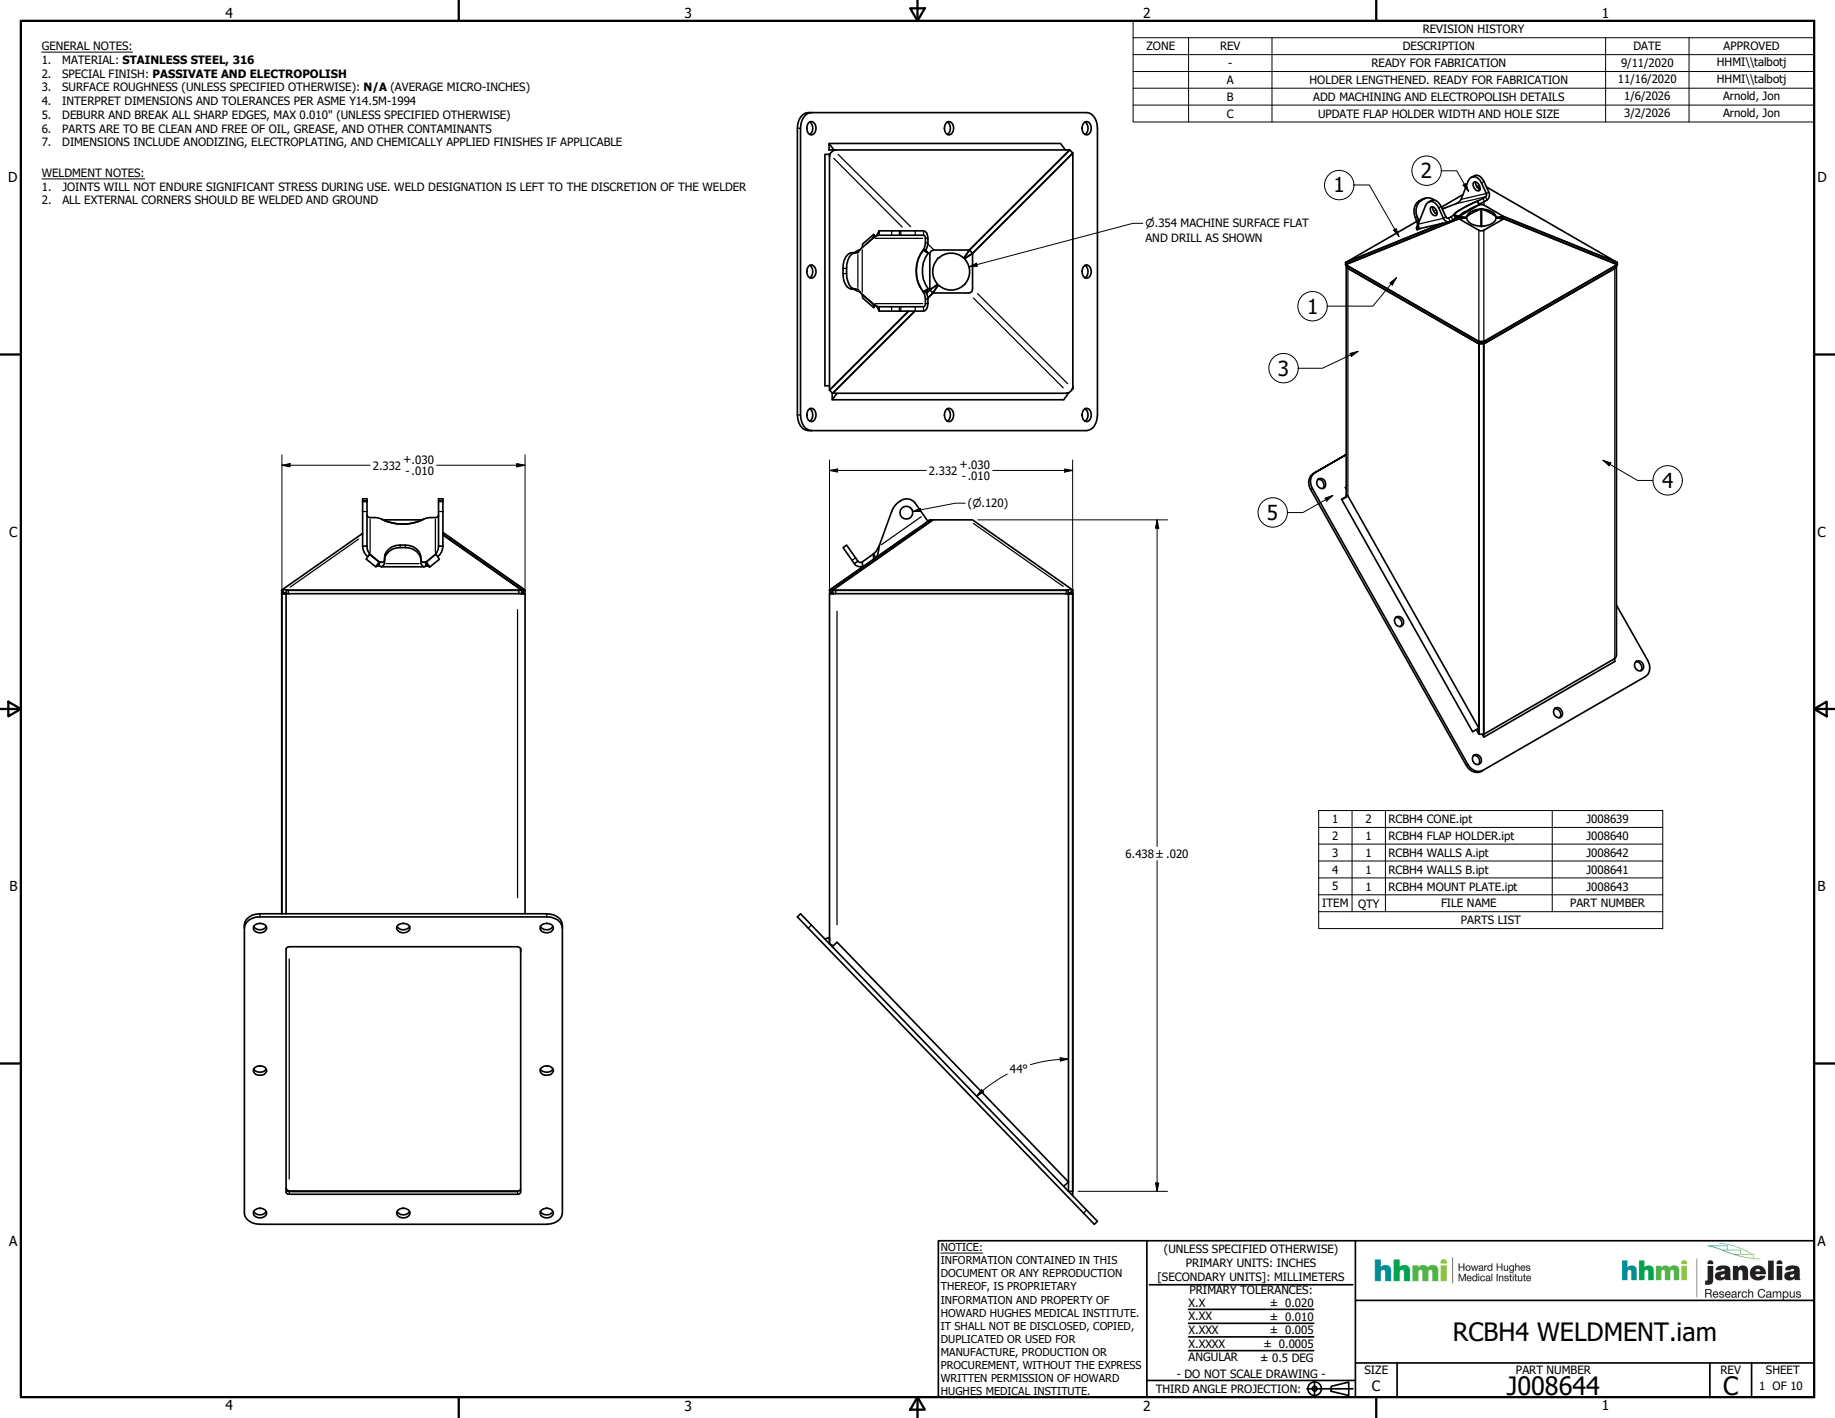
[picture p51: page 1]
PARTS LIST; PART NUMBER; 1 OF 10 THIRD ANGLE PROJECTION:; ± 0.5 DEG; RCBH4 WELDMENT.iam; REVISION HISTORY; WELDMENT NOTES:

GENERAL NOTES:
1. MATERIAL: STAINLESS STEEL, 316
2. SPECIAL FINISH: PASSIVATE AND ELECTROPOLISH
3. SURFACE ROUGHNESS (UNLESS SPECIFIED OTHERWISE): N/A (AVERAGE MICRO-INCHES)
4. INTERPRET DIMENSIONS AND TOLERANCES PER ASME Y14.5M-1994
5. DEBURR AND BREAK ALL SHARP EDGES, MAX 0.010" (UNLESS SPECIFIED OTHERWISE)
6. PARTS ARE TO BE CLEAN AND FREE OF OIL, GREASE, AND OTHER CONTAMINANTS
7. DIMENSIONS INCLUDE ANODIZING, ELECTROPLATING, AND CHEMICALLY APPLIED FINISHES IF APPLICABLE

ZONE | REV | DESCRIPTION | DATE | APPROVED

- | READY FOR FABRICATION | 9/11/2020 | HHMI\\talbotj
A | HOLDER LENGTHENED. READY FOR FABRICATION | 11/16/2020 | HHMI\\talbotj
B | ADD MACHINING AND ELECTROPOLISH DETAILS | 1/6/2026 | Arnold, Jon
C | UPDATE FLAP HOLDER WIDTH AND HOLE SIZE | 3/2/2026 | Arnold, Jon

1. JOINTS WILL NOT ENDURE SIGNIFICANT STRESS DURING USE. WELD DESIGNATION IS LEFT TO THE DISCRETION OF THE WELDER
2. ALL EXTERNAL CORNERS SHOULD BE WELDED AND GROUND

⌀.354 MACHINE SURFACE FLAT
AND DRILL AS SHOWN

1 | 2 | RCBH4 CONE.ipt | J008639
2 | 1 | RCBH4 FLAP HOLDER.ipt | J008640
3 | 1 | RCBH4 WALLS A.ipt | J008642
4 | 1 | RCBH4 WALLS B.ipt | J008641
5 | 1 | RCBH4 MOUNT PLATE.ipt | J008643
ITEM | QTY | FILE NAME | PART NUMBER

NOTICE:
INFORMATION CONTAINED IN THIS
DOCUMENT OR ANY REPRODUCTION
THEREOF, IS PROPRIETARY
INFORMATION AND PROPERTY OF
HOWARD HUGHES MEDICAL INSTITUTE.
IT SHALL NOT BE DISCLOSED, COPIED,
DUPLICATED OR USED FOR
MANUFACTURE, PRODUCTION OR
PROCUREMENT, WITHOUT THE EXPRESS
WRITTEN PERMISSION OF HOWARD
HUGHES MEDICAL INSTITUTE.

(UNLESS SPECIFIED OTHERWISE)
PRIMARY UNITS: INCHES
[SECONDARY UNITS]: MILLIMETERS
PRIMARY TOLERANCES:
X.XXX
X.XXXX
ANGULAR
- DO NOT SCALE DRAWING -

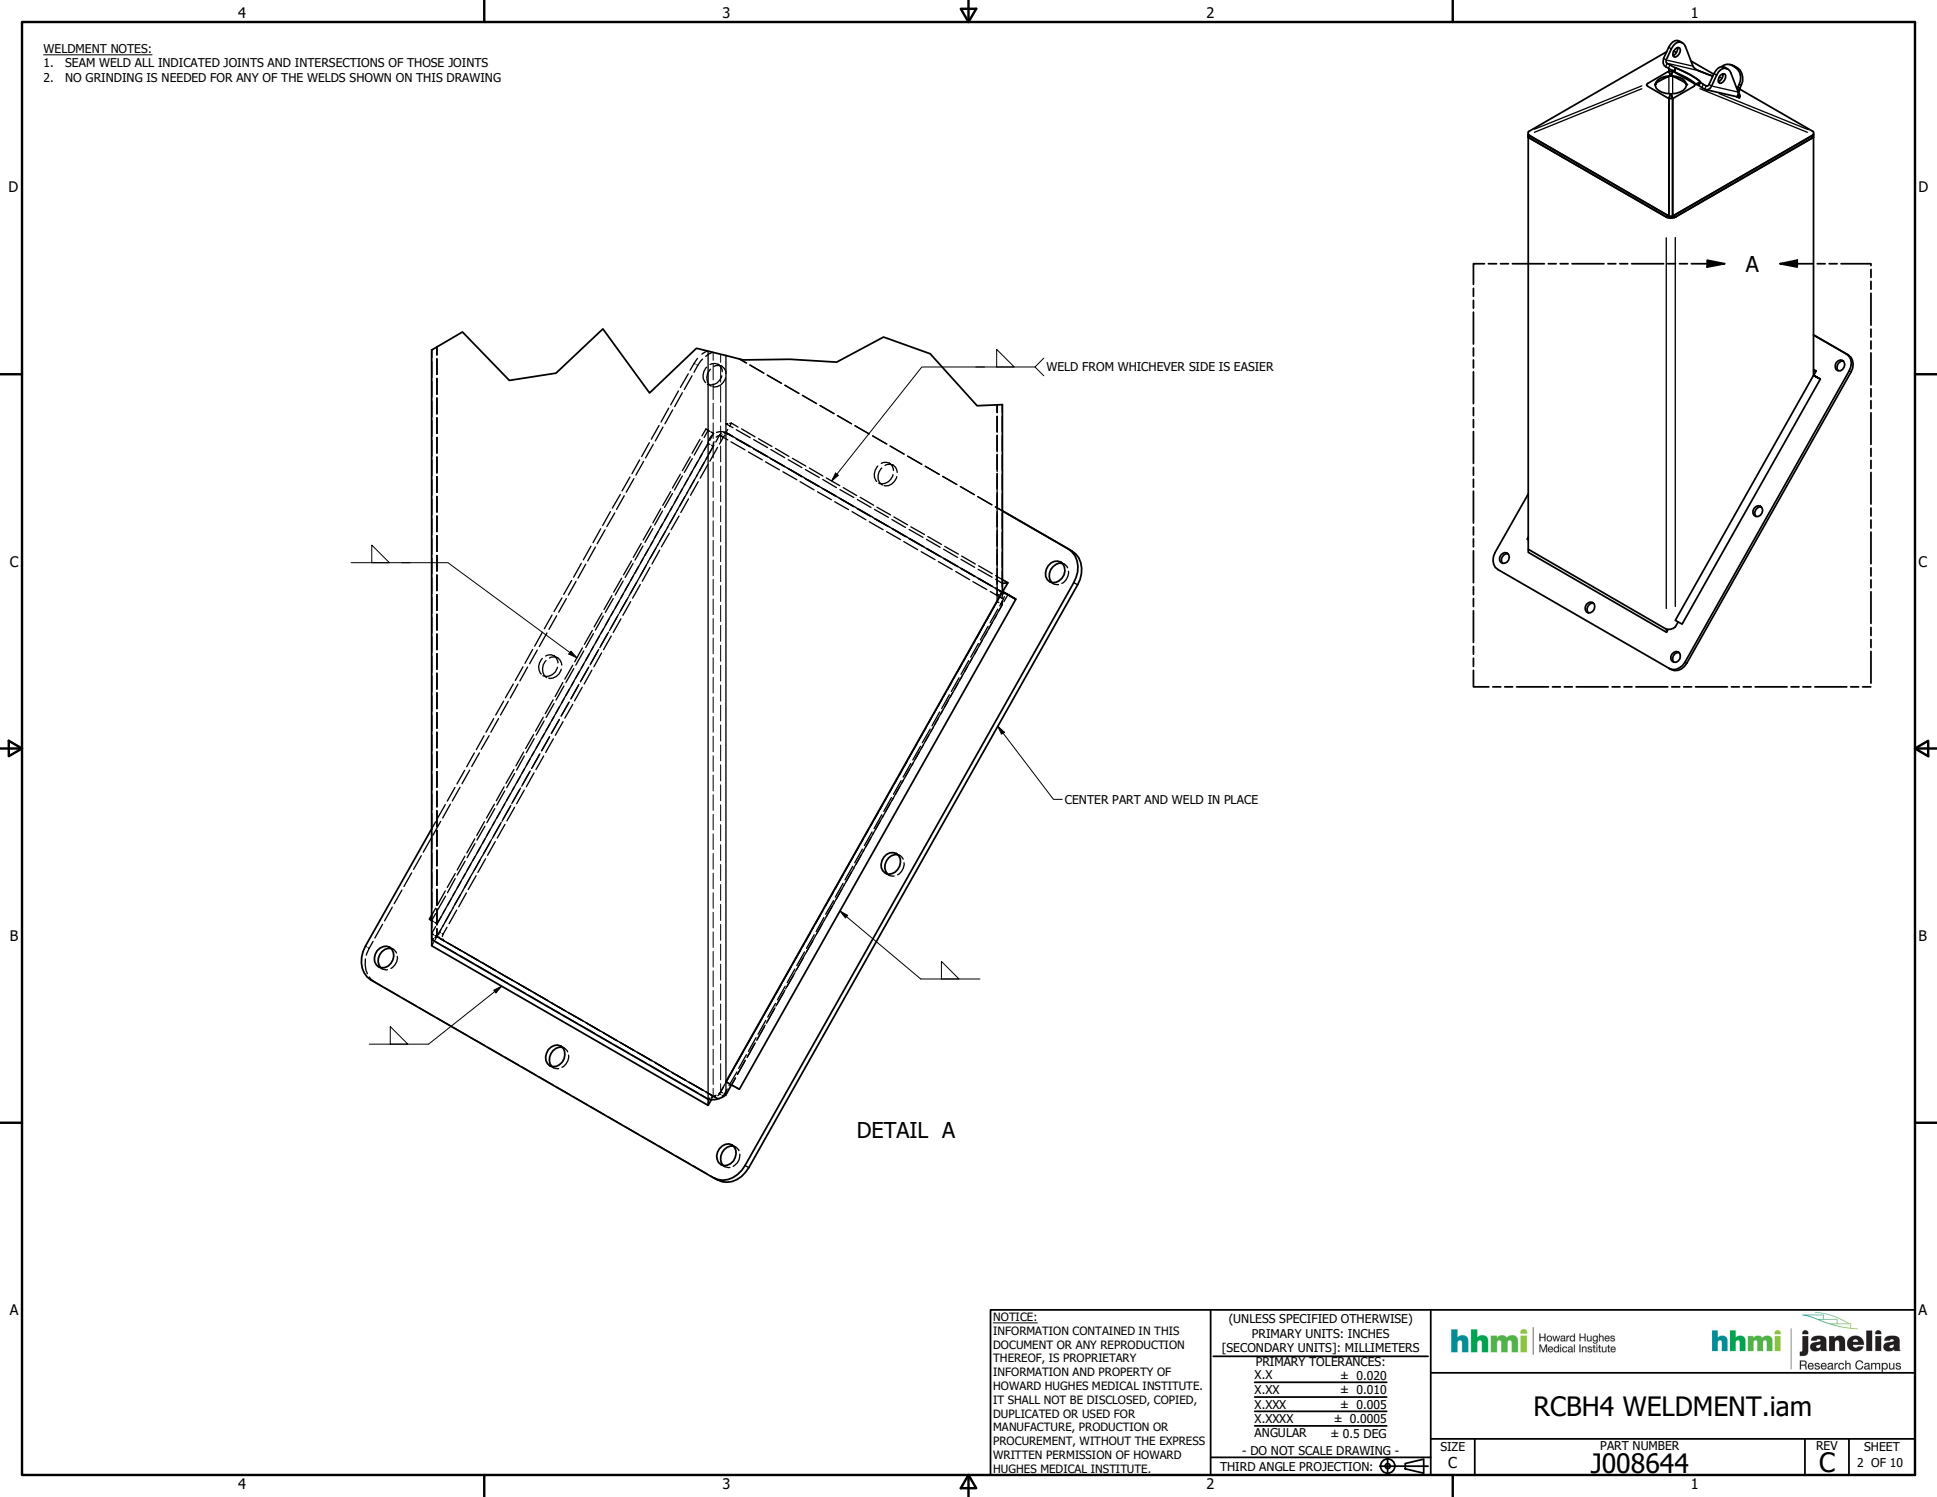
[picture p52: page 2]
DETAIL A; 2 OF 10 THIRD ANGLE PROJECTION:

WELDMENT NOTES:
1. SEAM WELD ALL INDICATED JOINTS AND INTERSECTIONS OF THOSE JOINTS
2. NO GRINDING IS NEEDED FOR ANY OF THE WELDS SHOWN ON THIS DRAWING

WELD FROM WHICHEVER SIDE IS EASIER

CENTER PART AND WELD IN PLACE

NOTICE:
INFORMATION CONTAINED IN THIS
DOCUMENT OR ANY REPRODUCTION
THEREOF, IS PROPRIETARY

(UNLESS SPECIFIED OTHERWISE)
PRIMARY UNITS: INCHES
[SECONDARY UNITS]: MILLIMETERS
PRIMARY TOLERANCES:

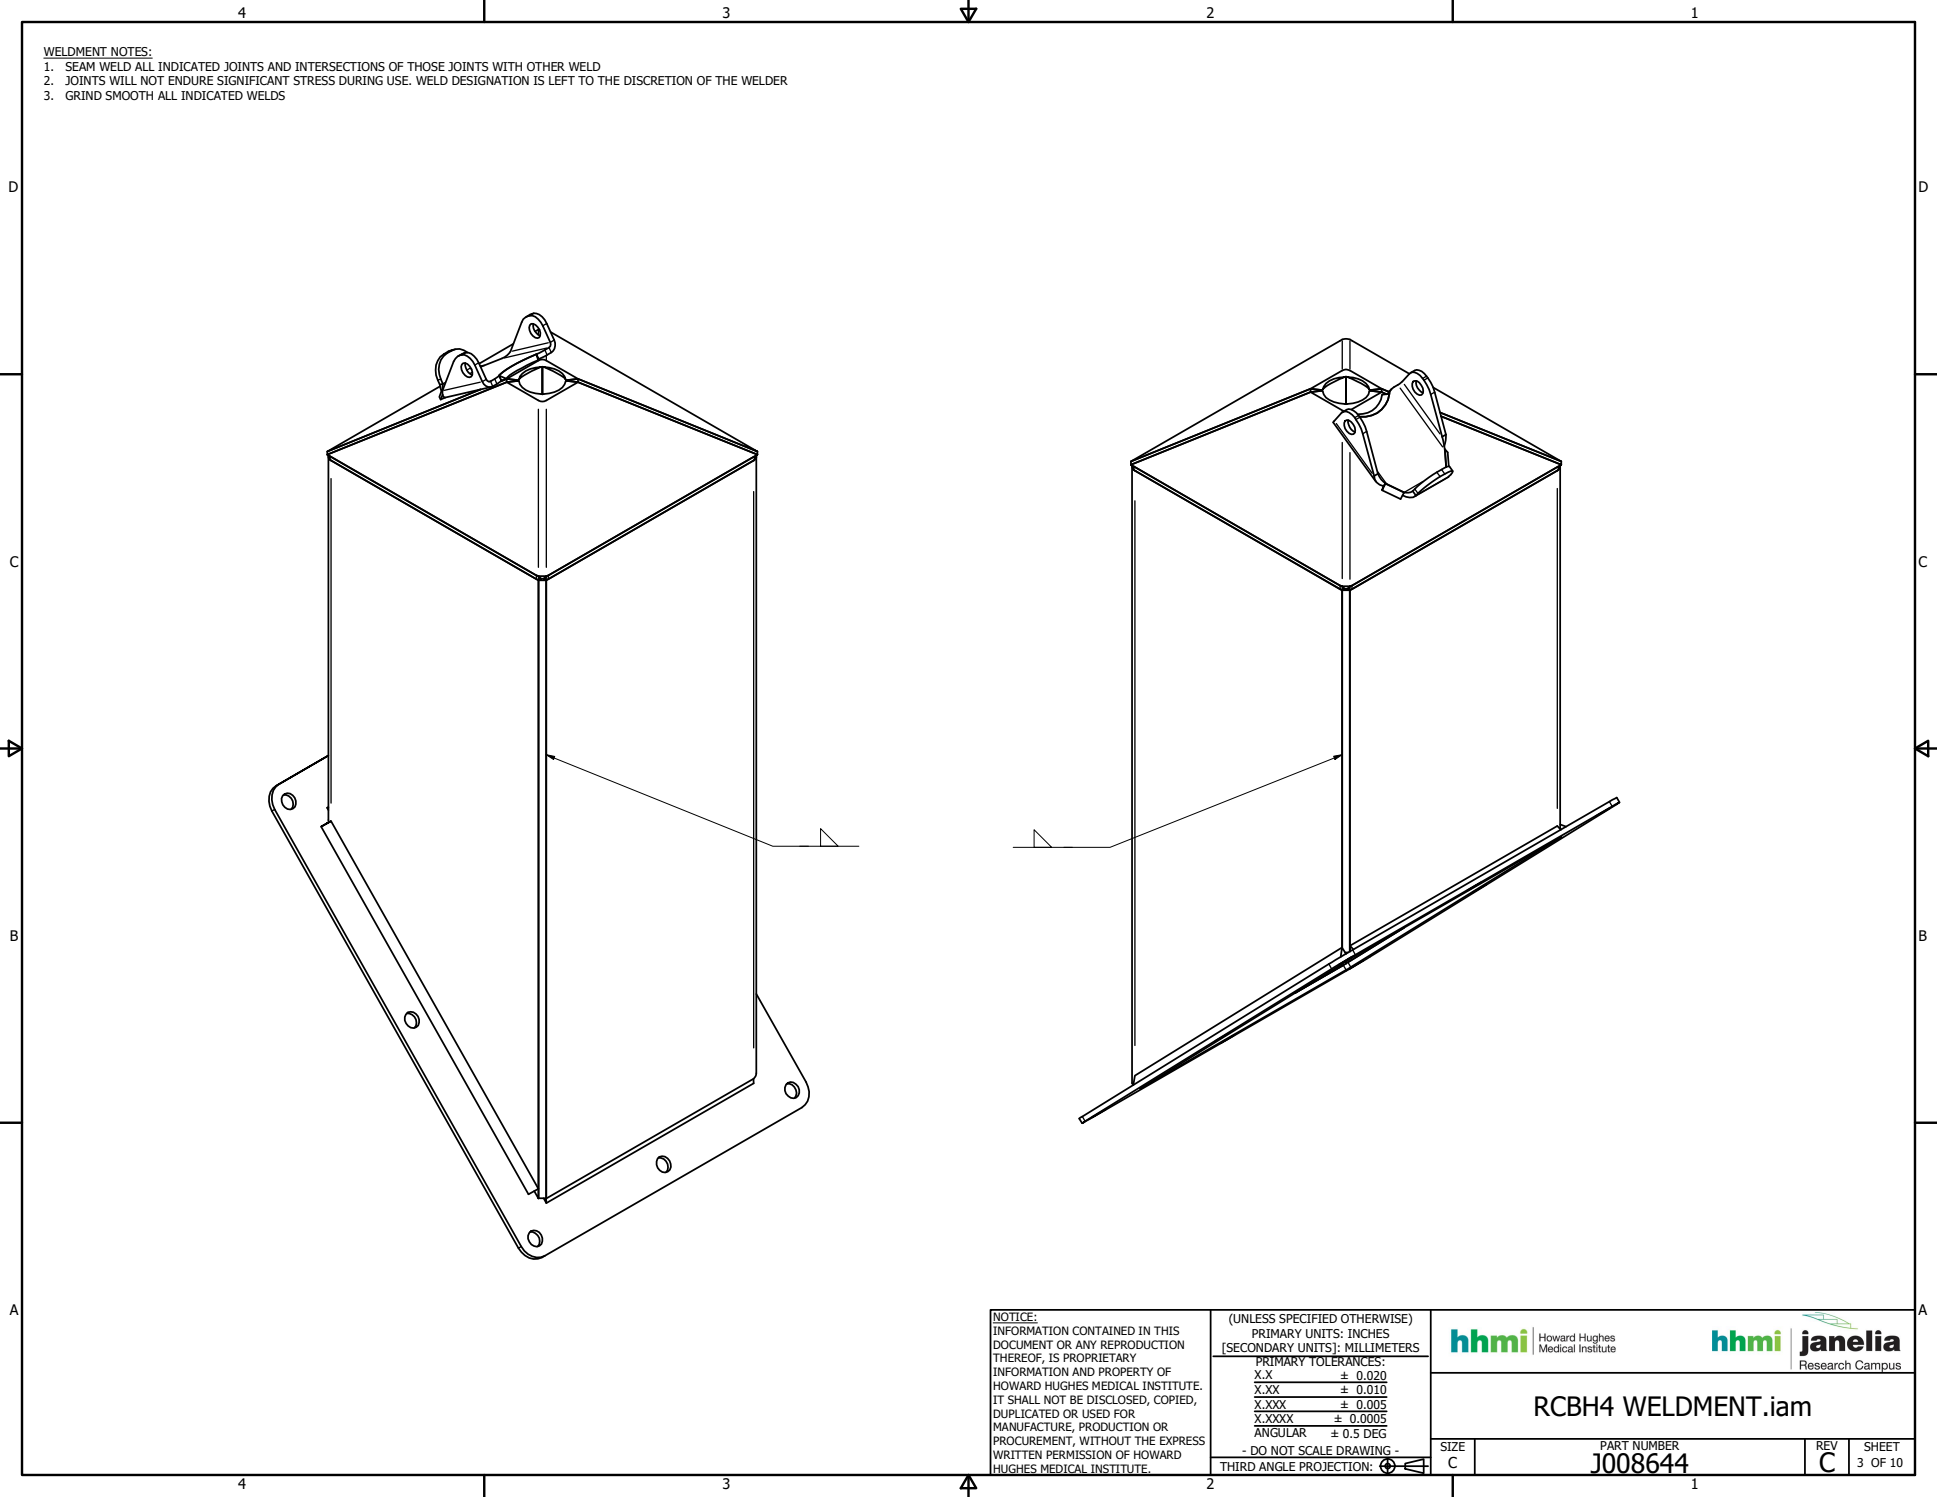
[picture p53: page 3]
3 OF 10 THIRD ANGLE PROJECTION:

1. SEAM WELD ALL INDICATED JOINTS AND INTERSECTIONS OF THOSE JOINTS WITH OTHER WELD
2. JOINTS WILL NOT ENDURE SIGNIFICANT STRESS DURING USE. WELD DESIGNATION IS LEFT TO THE DISCRETION OF THE WELDER
3. GRIND SMOOTH ALL INDICATED WELDS

NOTICE:
INFORMATION CONTAINED IN THIS
DOCUMENT OR ANY REPRODUCTION
THEREOF, IS PROPRIETARY

(UNLESS SPECIFIED OTHERWISE)
PRIMARY UNITS: INCHES
[SECONDARY UNITS]: MILLIMETERS
PRIMARY TOLERANCES:

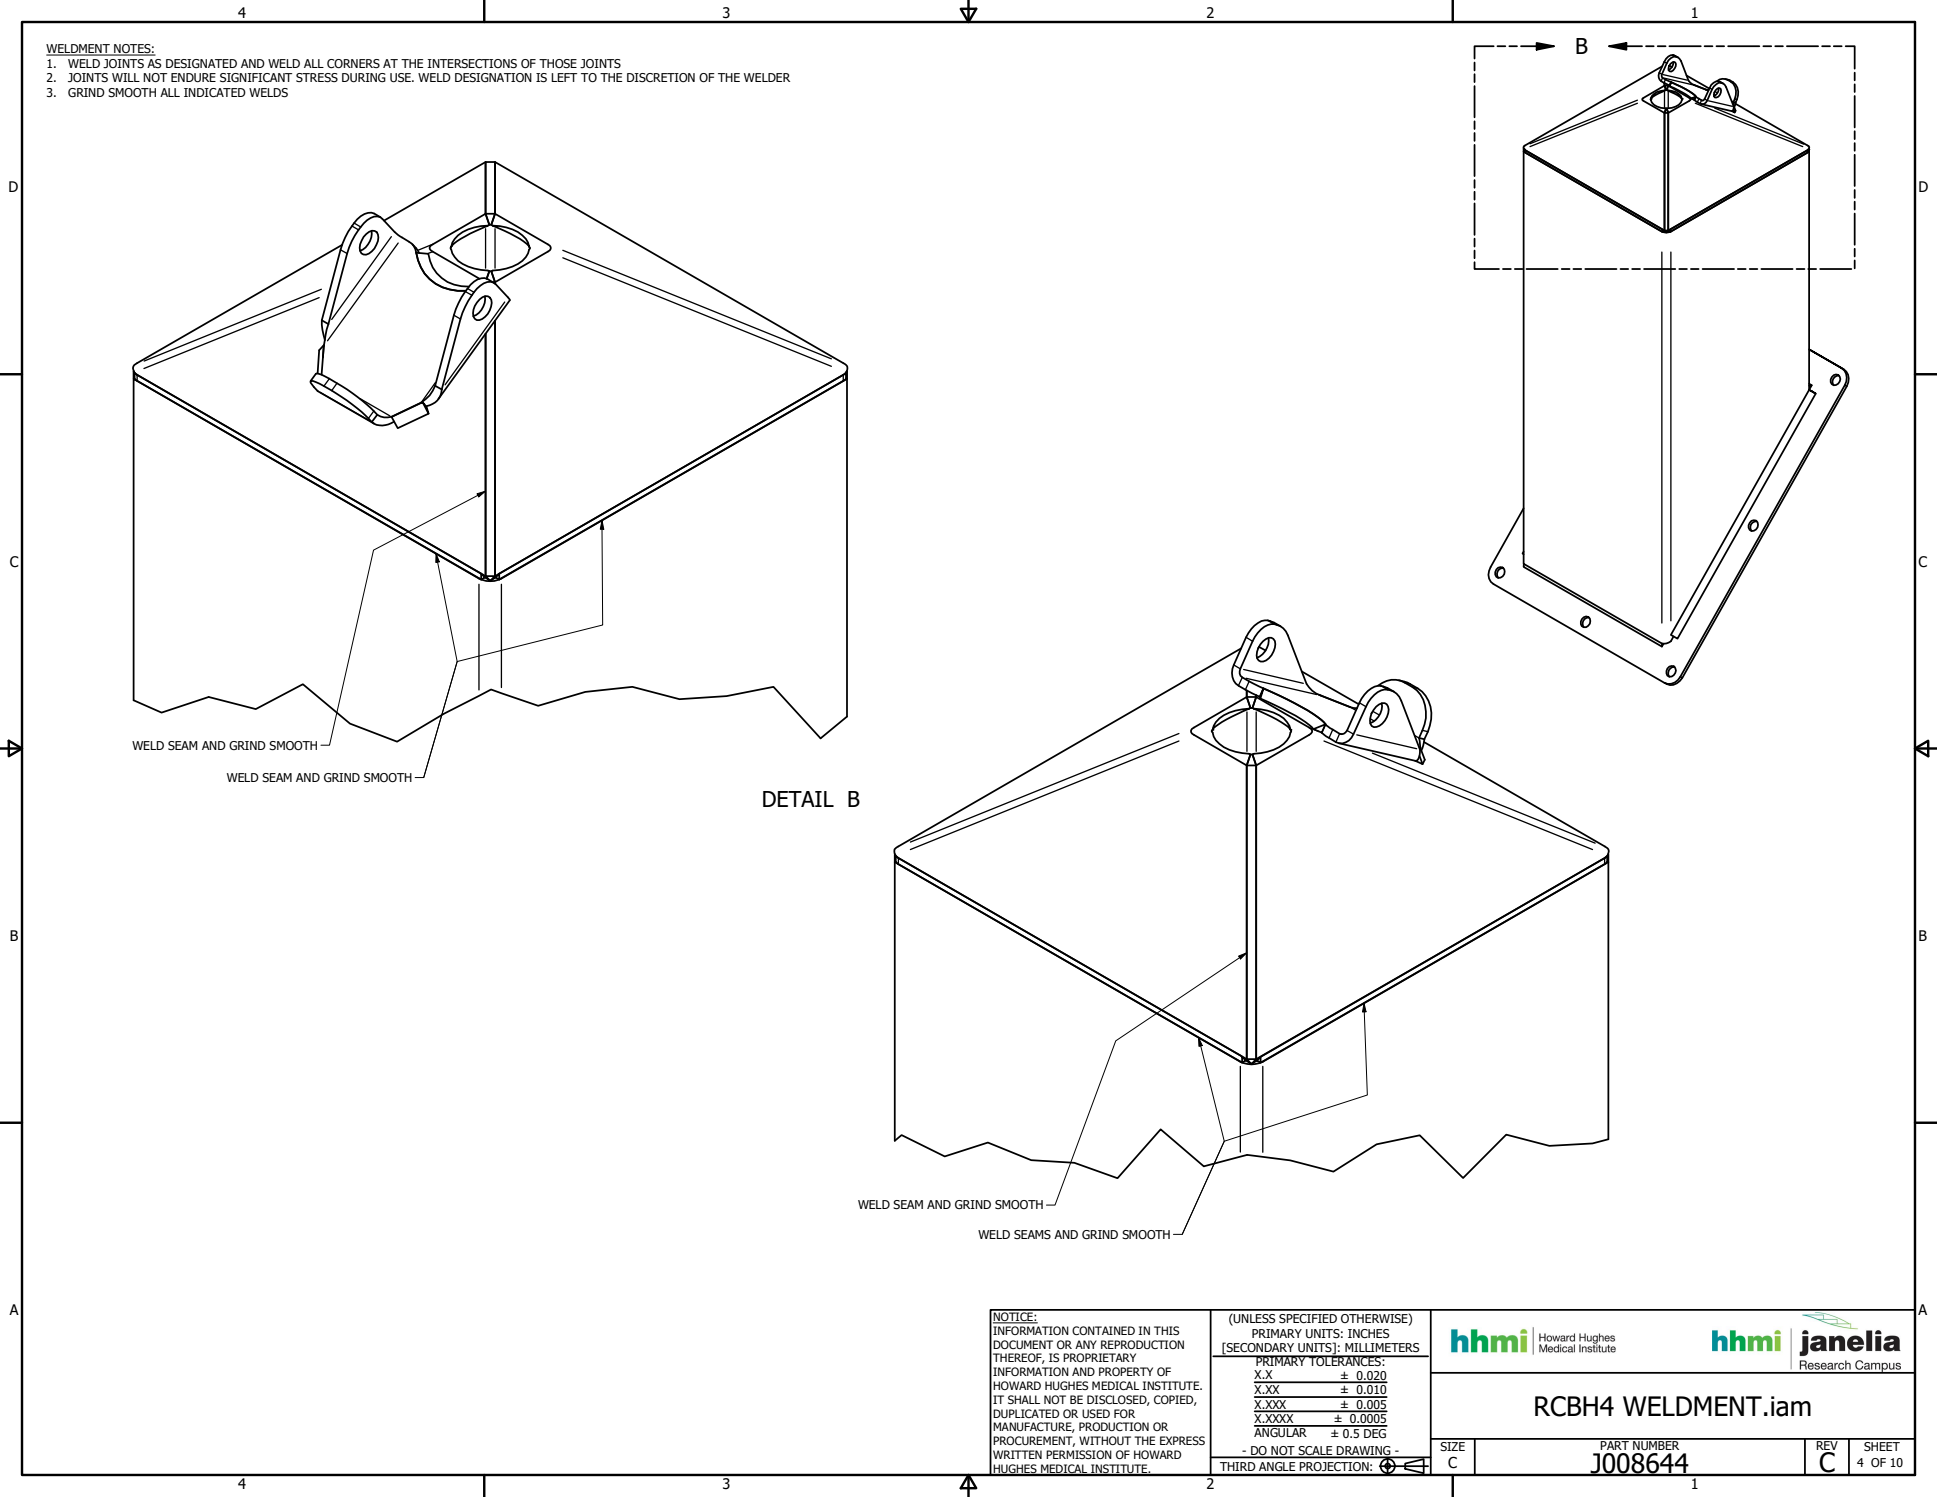
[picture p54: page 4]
DETAIL B; 4 OF 10 THIRD ANGLE PROJECTION:

1. WELD JOINTS AS DESIGNATED AND WELD ALL CORNERS AT THE INTERSECTIONS OF THOSE JOINTS
2. JOINTS WILL NOT ENDURE SIGNIFICANT STRESS DURING USE. WELD DESIGNATION IS LEFT TO THE DISCRETION OF THE WELDER
3. GRIND SMOOTH ALL INDICATED WELDS

WELD SEAM AND GRIND SMOOTH

WELD SEAMS AND GRIND SMOOTH

NOTICE:
INFORMATION CONTAINED IN THIS
DOCUMENT OR ANY REPRODUCTION
THEREOF, IS PROPRIETARY

(UNLESS SPECIFIED OTHERWISE)
PRIMARY UNITS: INCHES
[SECONDARY UNITS]: MILLIMETERS
PRIMARY TOLERANCES:

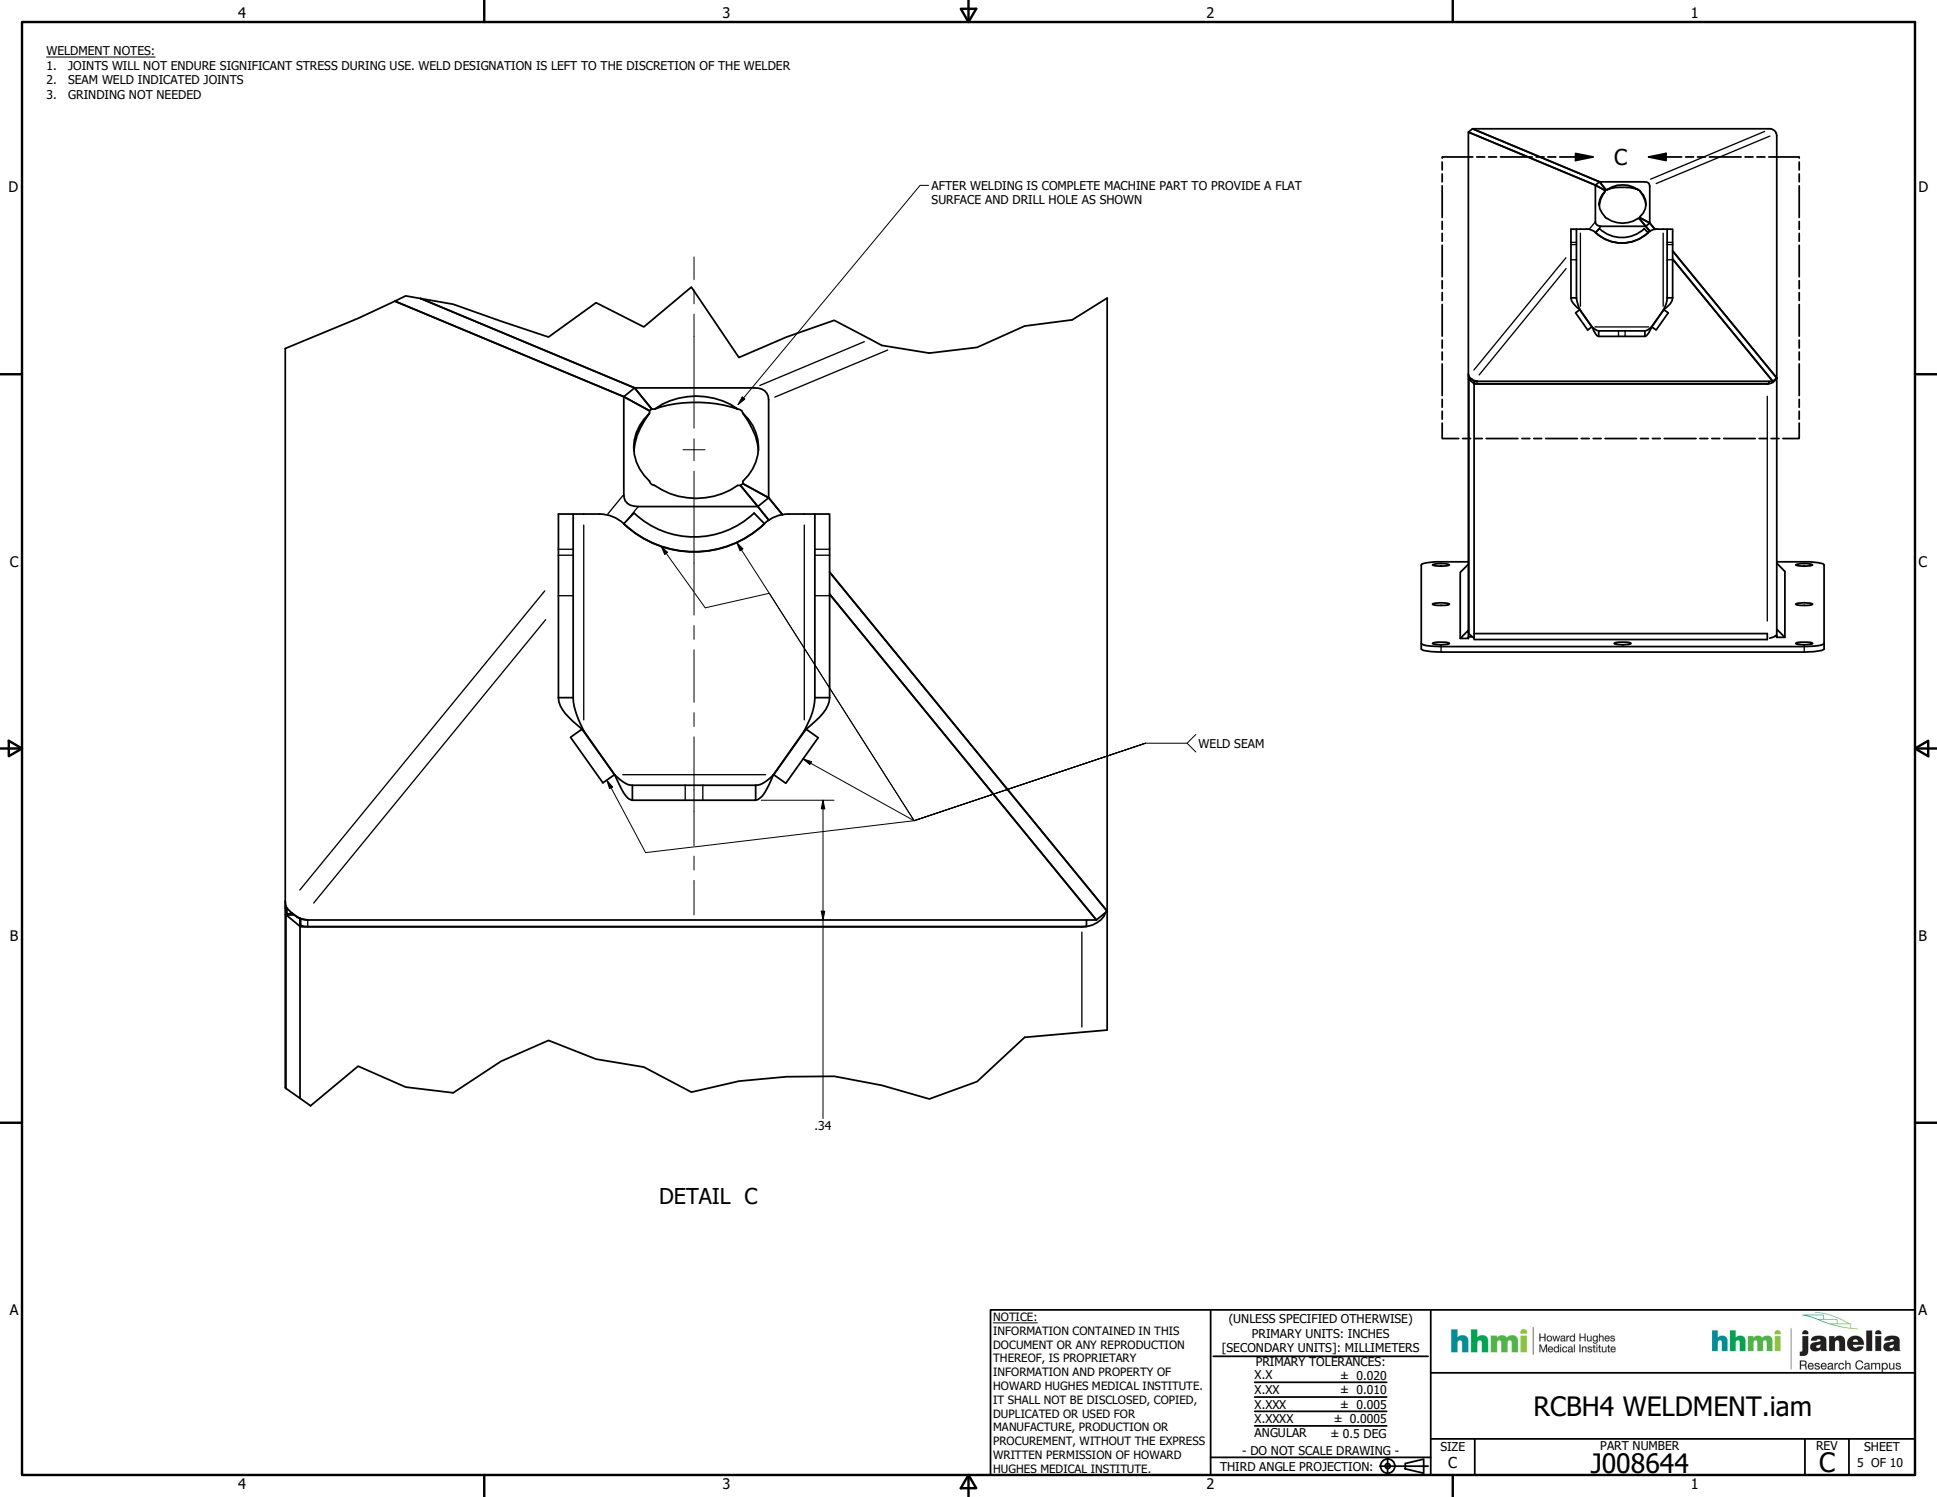
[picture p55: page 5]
DETAIL C; 5 OF 10 THIRD ANGLE PROJECTION:; WELD SEAM

1. JOINTS WILL NOT ENDURE SIGNIFICANT STRESS DURING USE. WELD DESIGNATION IS LEFT TO THE DISCRETION OF THE WELDER
2. SEAM WELD INDICATED JOINTS
3. GRINDING NOT NEEDED

AFTER WELDING IS COMPLETE MACHINE PART TO PROVIDE A FLAT
SURFACE AND DRILL HOLE AS SHOWN

NOTICE:
INFORMATION CONTAINED IN THIS
DOCUMENT OR ANY REPRODUCTION
THEREOF, IS PROPRIETARY

(UNLESS SPECIFIED OTHERWISE)
PRIMARY UNITS: INCHES
[SECONDARY UNITS]: MILLIMETERS
PRIMARY TOLERANCES:

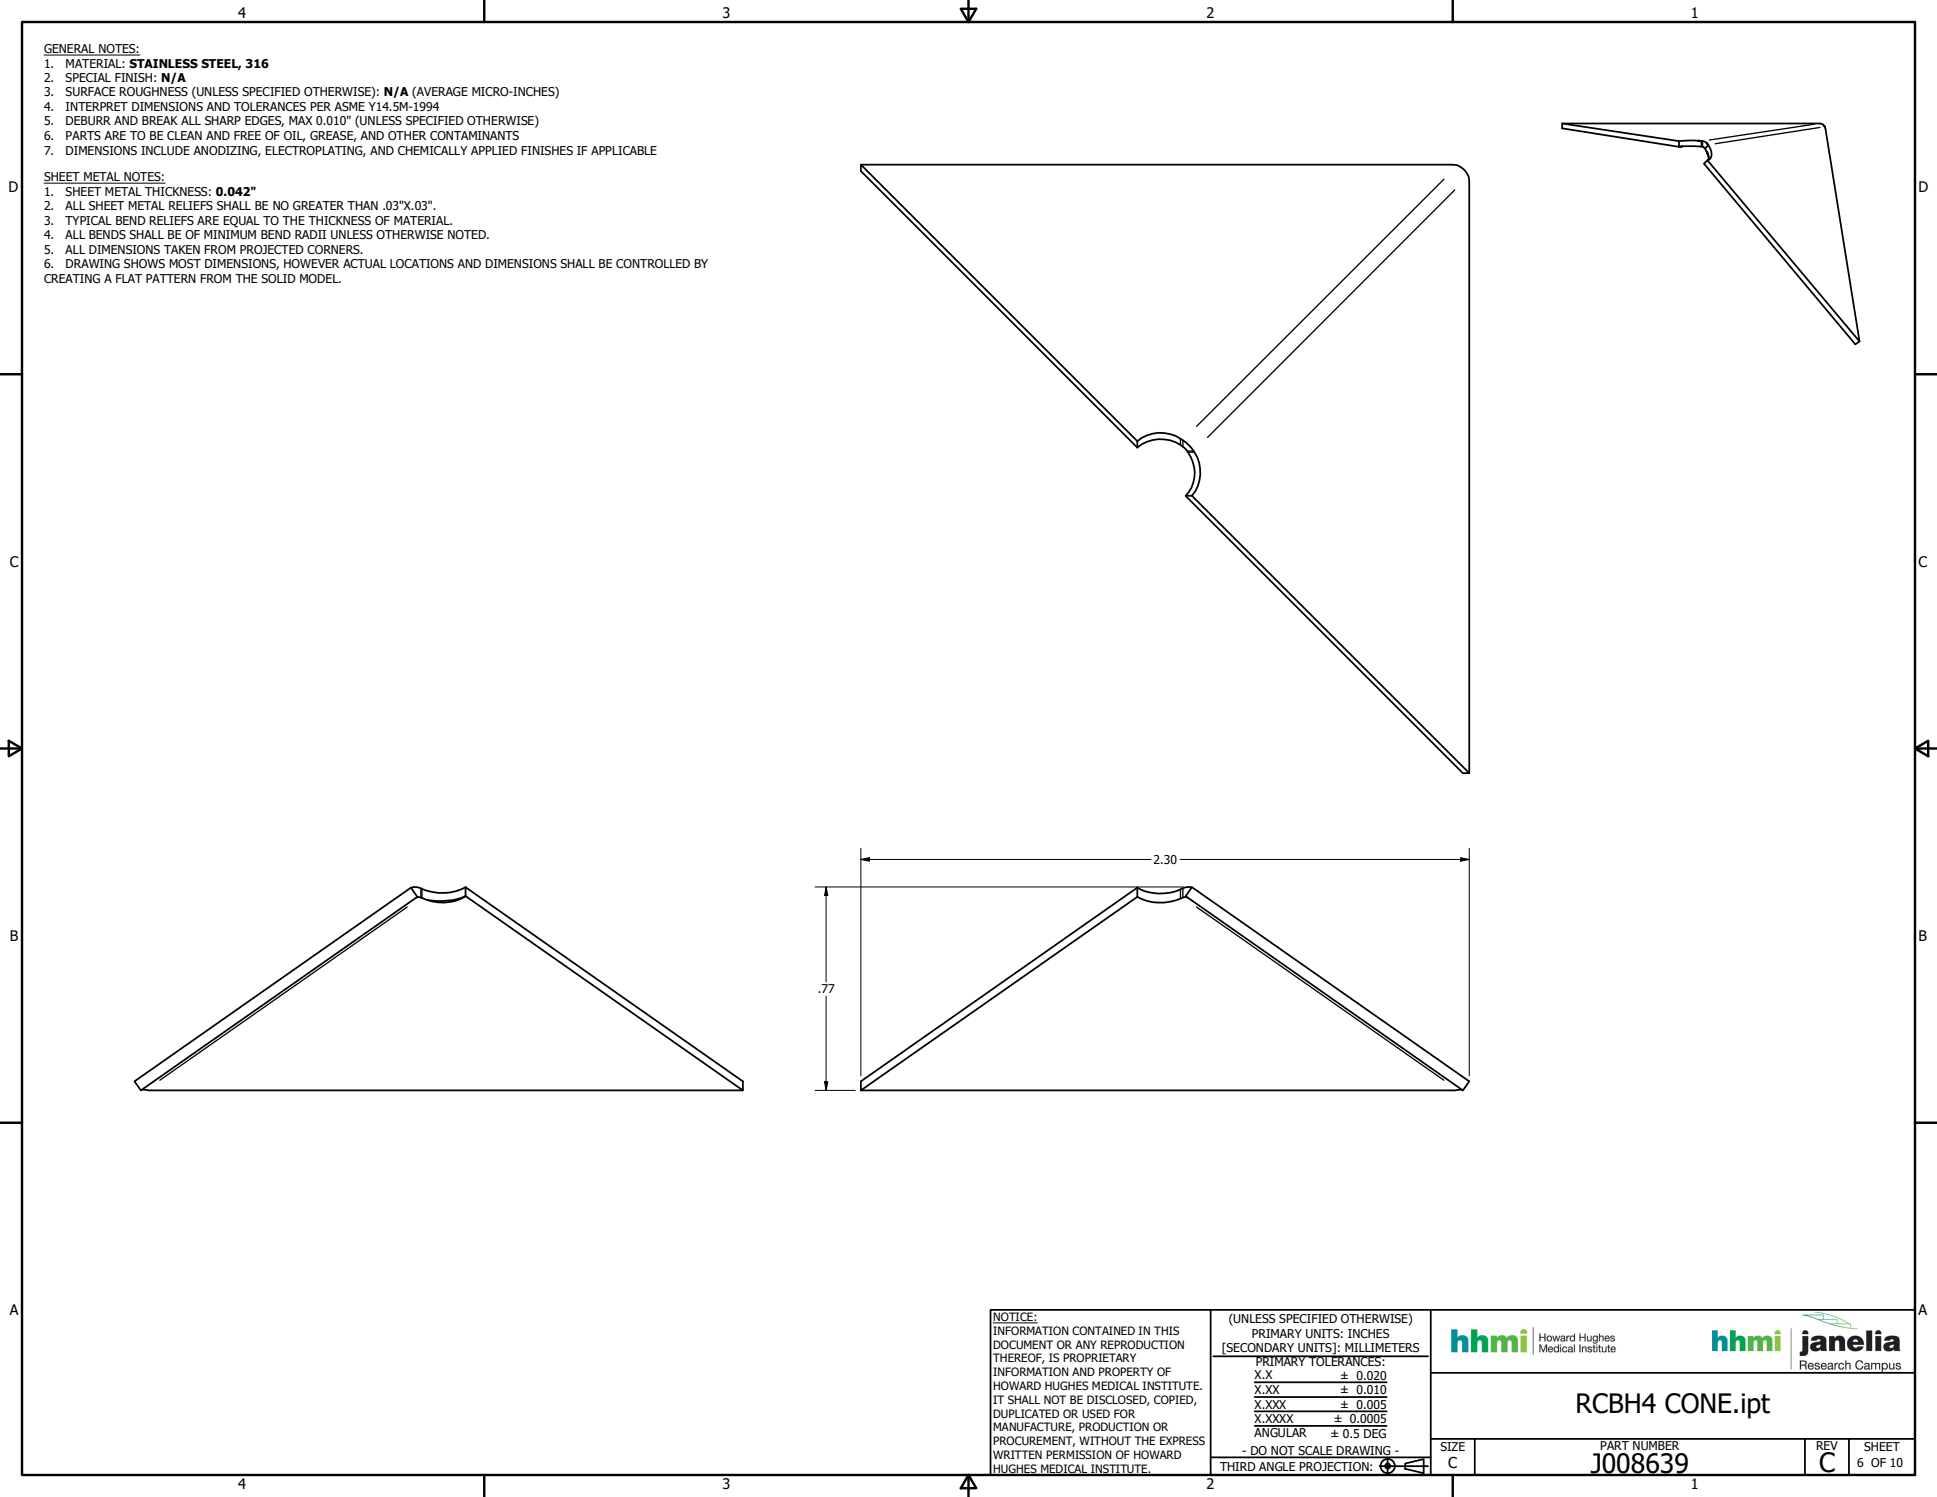
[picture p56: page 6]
6 OF 10 THIRD ANGLE PROJECTION:; RCBH4 CONE.ipt; 2. SPECIAL FINISH: N/A

6. PARTS ARE TO BE CLEAN AND FREE OF OIL, GREASE, AND OTHER CONTAMINANTS
7. DIMENSIONS INCLUDE ANODIZING, ELECTROPLATING, AND CHEMICALLY APPLIED FINISHES IF APPLICABLE

SHEET METAL NOTES:

1. SHEET METAL THICKNESS: 0.042"
2. ALL SHEET METAL RELIEFS SHALL BE NO GREATER THAN .03"X.03".
3. TYPICAL BEND RELIEFS ARE EQUAL TO THE THICKNESS OF MATERIAL.
4. ALL BENDS SHALL BE OF MINIMUM BEND RADII UNLESS OTHERWISE NOTED.
5. ALL DIMENSIONS TAKEN FROM PROJECTED CORNERS.
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

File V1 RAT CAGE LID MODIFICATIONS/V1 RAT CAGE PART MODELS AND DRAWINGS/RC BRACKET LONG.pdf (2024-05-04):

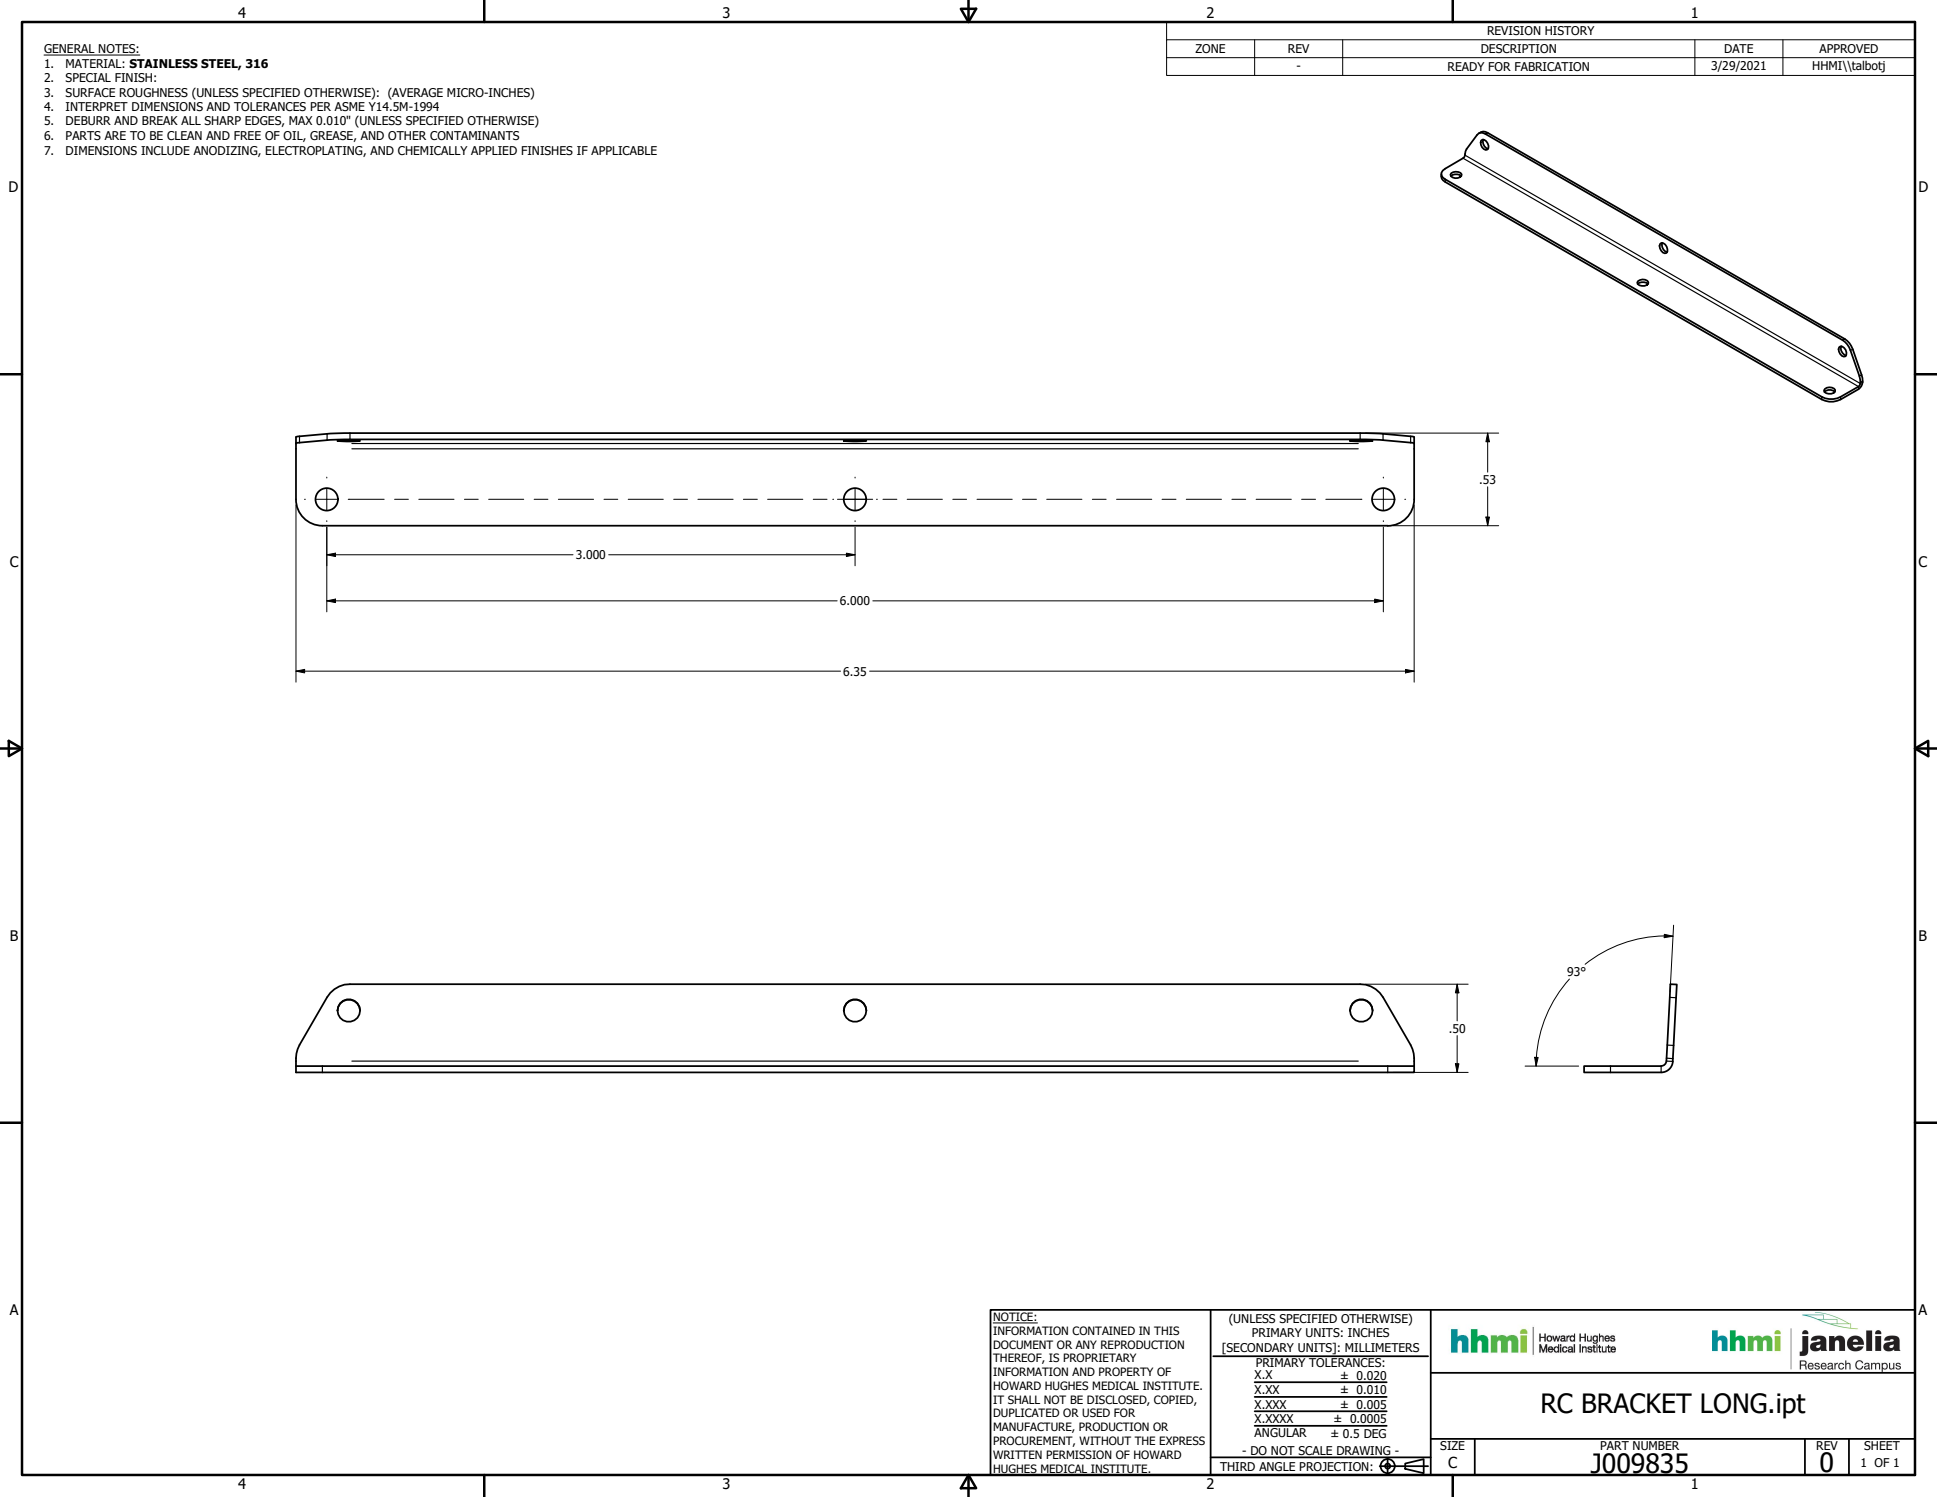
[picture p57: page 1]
PART NUMBER; 1 OF 1 THIRD ANGLE PROJECTION:; ± 0.020 ± 0.010 ± 0.005 ± 0.0005 ± 0.5 DEG; REVISION HISTORY

GENERAL NOTES:
1. MATERIAL: STAINLESS STEEL, 316
2. SPECIAL FINISH:
3. SURFACE ROUGHNESS (UNLESS SPECIFIED OTHERWISE): (AVERAGE MICRO-INCHES)
4. INTERPRET DIMENSIONS AND TOLERANCES PER ASME Y14.5M-1994
5. DEBURR AND BREAK ALL SHARP EDGES, MAX 0.010" (UNLESS SPECIFIED OTHERWISE)
6. PARTS ARE TO BE CLEAN AND FREE OF OIL, GREASE, AND OTHER CONTAMINANTS
7. DIMENSIONS INCLUDE ANODIZING, ELECTROPLATING, AND CHEMICALLY APPLIED FINISHES IF APPLICABLE

ZONE | REV | DESCRIPTION | DATE | APPROVED

- | READY FOR FABRICATION | 3/29/2021 | HHMI\\talbotj

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

RC BRACKET LONG.ipt

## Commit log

2024-05-09 Create sub folders for V1 and V2 changes
    [CARD HOLDER BRACKET J010308.stp, CARD HOLDER BRACKET.dwg, CARD HOLDER BRACKET.ipt, RAT WATER BOTTLE TRANSITION.dwg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]
2024-05-29 Add drawings and updated instruction document
    [CARD HOLDER BRACKET J010308.stp, CARD HOLDER BRACKET.dwg, CARD HOLDER BRACKET.ipt, RC BRACKET FRONT.dwg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]
2026-03-02 Update RCBH4 files
    was rev A now rev C
    [RCBH4 WELDMENT revA.stp, RCBH4 WELDMENT revC.stp]
